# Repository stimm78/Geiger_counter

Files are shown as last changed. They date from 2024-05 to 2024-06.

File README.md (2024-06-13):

# Geiger Counter

 A Geiger counter is a practical electronic device used to measure ionizing radiation, and it is widely used in experimental physics and nuclear industries. Our goal for this project was to build a custom Geiger counter to measure the count rate of radioactive sources. After building the Geiger counter, we characterized various parameters of our device such as the dead time and tube efficiency. Using our device, we measured and compared the count rates of Co60 and Sr90 with attenuating materials placed in between the device and the radioactive source. 

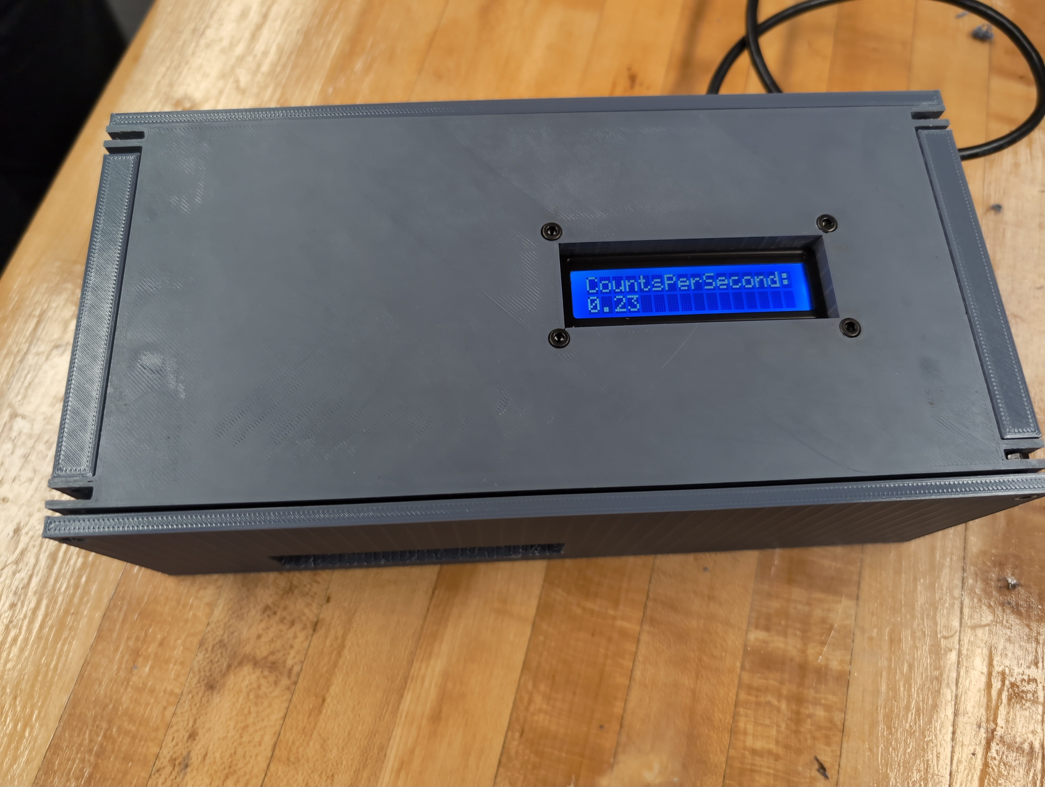
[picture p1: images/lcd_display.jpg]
alt test

  
  ## Table of Contents
* [Motivation](https://github.com/stimm78/Geiger_counter#motivation)
* [Theory](https://github.com/stimm78/Geiger_counter#theory)
* [Design](https://github.com/stimm78/Geiger_counter#design)
* [Device Characterization](https://github.com/stimm78/Geiger_counter#device-characterization)
* [Experiments](https://github.com/stimm78/Geiger_counter#experiments)
* [Acknowledgements](https://github.com/stimm78/Geiger_counter#acknowledgements)

## Motivation
The radiation we are observing is ionizing radiation, carriers of enough energy to ionize many common materials. The lower bound for this energy is considered to be about 10 eV, which encompasses alpha particles (He nuclei), beta particles (electrons), and gamma rays (photons). These subatomic particles are not visible to the naked eye; to verify their existence and our physical models of their behavior, it is necessary to build specialized nuclear detector devices such as our geiger counter.

 In particular, our group was interested in testing the drop-off of the intensity of nuclear radiation with distance and with material thickness. We expect that the radiation emitted from our sources are isotropic, so the intensity is expected to drop off as $1/r^2$, where r is the distance from the source. By modeling the attenuation of radiation as being attributed to random scattering/absorption by the atoms of an attenuating material, we should also expect the intensity of ionizing radiation should drop off exponentially as $I = I_0e^{\mu t}$, where $I_0$ is the initial intensity of the radiation,  is the linear attenuation coefficient of our material, and t is the thickness of our material.

## Theory 

### Geiger Muller Tube


A GM counter is a nuclear detector which is capable of detecting alpha particles, beta particles, and gamma radiation. To detect these ionizing particles, the geiger counter is specially designed to amplify the electrical discharge from one ionized atom and read this discharge as a voltage drop across a resistor.

The Geiger Muller counter is a metallic tube with a tungsten rod connecting the anode and cathode, filled with a gaseous mixture primarily composed of noble gas with some organic compound like ethanol mixed within it. When we connect the cylinder to the negative terminal of a high voltage source, a large voltage gap is generated between the tungsten and the metallic cylinder, creating a large electric field within the tube. When ionizing radiation enters the tube and ionizes an atom, the released electron is accelerated by the electric field, gaining sufficient kinetic energy to further ionize other atoms, whose electron offspring get accelerated by the electric field, which ionizes more atoms, etc.. This positive feedback loop of ionization is called the Townsend Avalanche, which amplifies the electrical discharge until the electrons reach the central electrode to move along the body of the circuit. Meanwhile, the positive cations leftover from ionization are pushed away from the central electrode towards the outer metallic cylinder. Our impulse of current will then run through a resistor, creating a measurable voltage drop measurable by a detector. The current will the move along back to the end of the tube, recombining with the positive charges lingering on the metallic cylinder and resetting our tube to take further measurements.

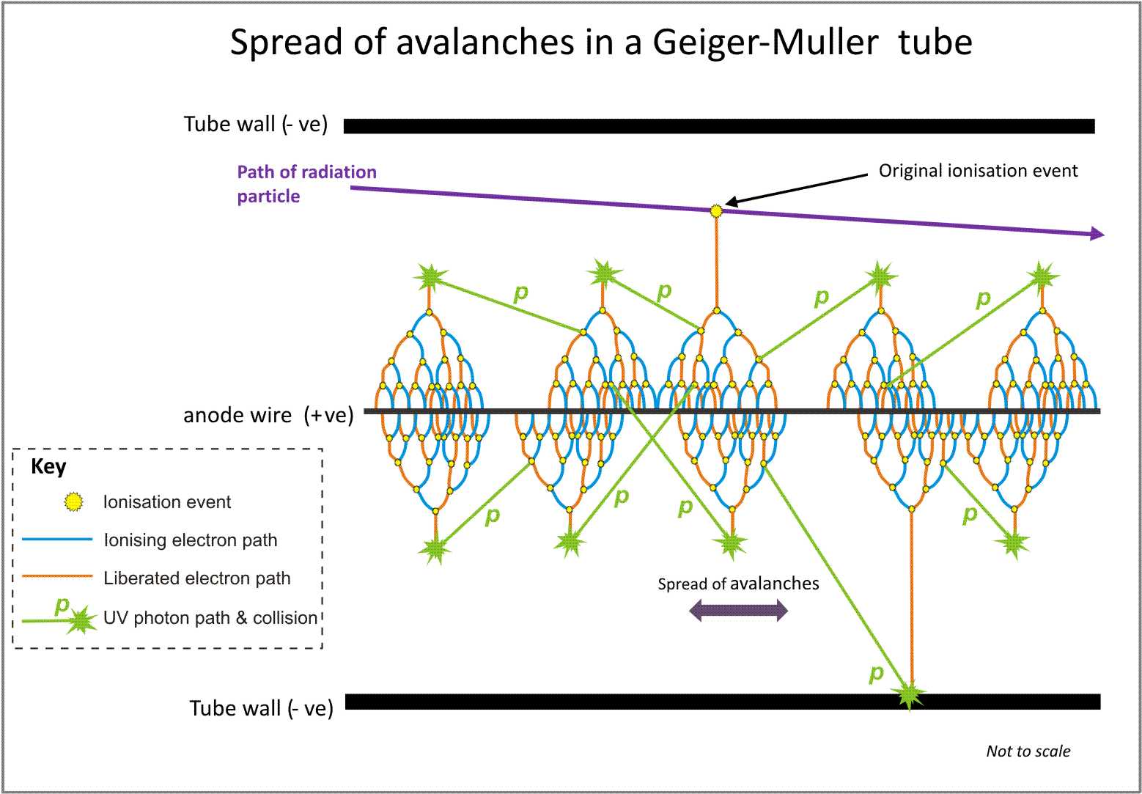
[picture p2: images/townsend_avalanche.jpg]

When ionizing radiation triggers the avalanche effect, the tube is temporarily unable to detect new radiation due to the time it takes for all the wonderful physics outlined above to run its course when a particle is detected. This temporary insensitivity to radiation is called the dead time of the counter. To maximize the reliability of our measurements, we should minimize the dead time. This is a key limitation to geiger counters - they are not accurate for extremely high counting rates, or equivalently when there are a high amount of nuclear particles striking the tube. Another limitation is that the Geiger counter cannot distinguish between the energies of two different nuclear particles; the current pulse generated by the tube is the same.

Some ionizing radiation will pass through the tube without ionizing any atoms, adding further uncertainty to our measurement of the radiation intensity. The ratio between the measured count rate from the geiger counter and the true one calculated from the activity level of our source is called the tube efficiency. This metric should be as high as possible to improve the reliability of our measurement.

Inverse Square Law Dropoff with Distance
If we model our radiation sources as emitting ionizing radiation isotropically, then necessarily the radiation emitted per second per steradians should be constant. Call this quantity I0. The area that some solid angle $\Omega$ consumes at a distance r is $\Omega r^2$; thus, the radiation emitted per second per unit area $I(r)$ is related to $I_0$ by

$$I(r)\Omega r^2 = I_0 \to I(r)=I_0/(r^2)$$

Thus, we should expect an inverse square law drop off in radiation intensity as we get further from a radioactive source.

Exponential Attenuation
Suppose that some $N(x)$ radioactive particles scatter off of the atoms within some infinitesimal thickness $dx$ with probability $\mu dx$, modeling the scattering cross section of the atoms within this slice of material. Then the number of radioactive particles remaining after scattering off of our slice of material is

$dN = -Ndx$, so then calling $N(0) = N_0$ and solving for $N(x)$
$$dN/N= -\mu dx \to ln(N/N_0)=-\mu x \to N(x)=N_0e^{-\mu x}$$
Thus, if our attenuating material is t long, then the number of radioactive particles that remain after passing through our material is
$N = N_0e^{-t}$, which naturally implies that $I = I_0e^{-t}$

## Design
### [Parts List](https://docs.google.com/spreadsheets/d/1FQi-imXlj1l_IscpUjg6qlx7No3eN8g5/edit?usp=sharing&ouid=113398199388474590846&rtpof=true&sd=true)

### Circuit Diagram
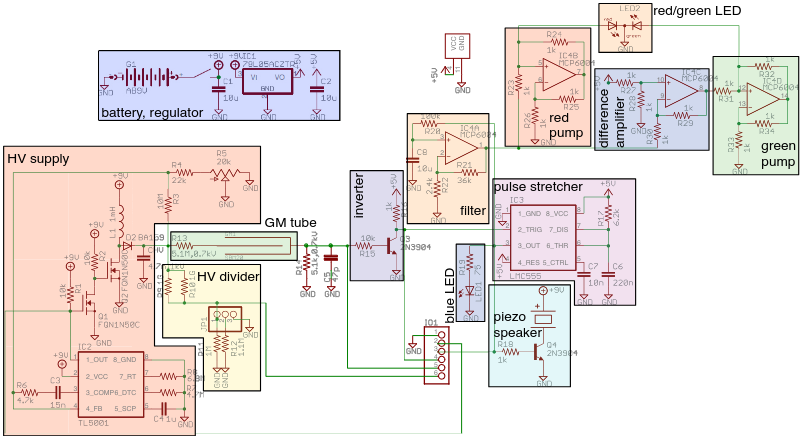
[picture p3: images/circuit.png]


We used a 9V battery source to power the circuit. The HV supply is achieved using a boost converter (TL5001) which steps the voltage up to 400V as required by the GM tube. When ionizing radiation is detected, the GM tube emits a current pulse which can be converted into a voltage pulse through a 5.1 kOhm resistor. The inverter is a BJT that acts as a switch to invert the voltage pulse.  Since these pulses are extremely short, the pulse stretcher (555 timer) converts the original pulse into a 1.5ms long square pulse. The blue LED will flash and the piezo speaker will click whenever a pulse is detected. The filter
smooths out voltage pulses and produces a voltage that is proportional to the count rate. The red and green current pumps convert the filtered voltage to a proportional current. The difference amplifier subtracts the filter voltage from a reference voltage, which causes the green LED to fade as the count rate increases. The RG LED serves as a visual indication of the count rate, with red corresponding to a high count rate and green corresponding to a low count rate.
### PCB
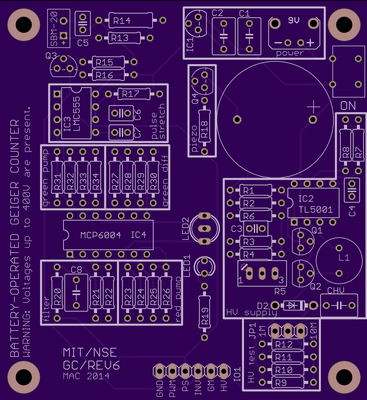
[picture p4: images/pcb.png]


We assembled these components onto a PCB that was designed and made available by [MIT](https://ocw.mit.edu/courses/22-s902-do-it-yourself-diy-geiger-counters-january-iap-2015/pages/labs/), with modifications to the HV supply in order to achieve the desired boost voltage. It turns out that the components around the HV booster designed by MIT do not work with the TL5001 chip, and we had to modify several components around the HV supply. We changed the resistors in the diagram to the following values: R8 = 500 KOhm, R7 = 460 KOhm, R4 = 10KOhm; Potentiometer: 10KOhm; R3 = 6.4 MOhm. This gave a range of voltage values across the GM tube from 320V to 480V, which we could tune using the potentiometer. The GM tube we used is the SBM-20 GM tube, which has an operating voltage range of 375-475 Volts.



### Counting Rate
The expected count rate is the inverse of the average time between counts (these times follow an exponential distribution; see Experimental Method). We used an Arduino UNO to calculate the difference in times between counts and determine the displayed rate. The rate considers the 20 latest counts, allowing it to update to any changes in its surroundings. To compensate for any sharp decrease in count, the rate removes the oldest count from consideration after twice the average of the considered times (for the exponential distribution, this time is equal to the average time plus one standard deviation). To display the counting rate, we used an LCD connected to the Arduino.

### 3D Printed Case
We 3D printed a case to contain and mount the parts of our counter. It is composed of three parts: the base, with inserts for the PCB, Arduino, battery holder, and GM tube clips; the outer case, with the outer face of the GM tube window approximately one inch away from the GM tube; and the lid, with an insert for the display.

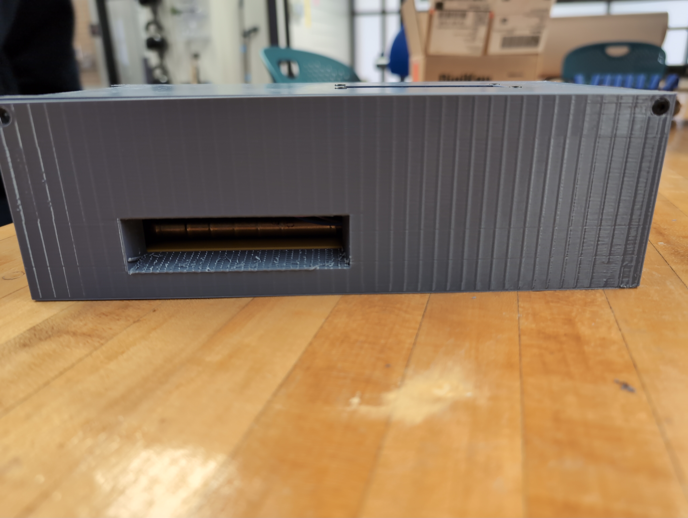
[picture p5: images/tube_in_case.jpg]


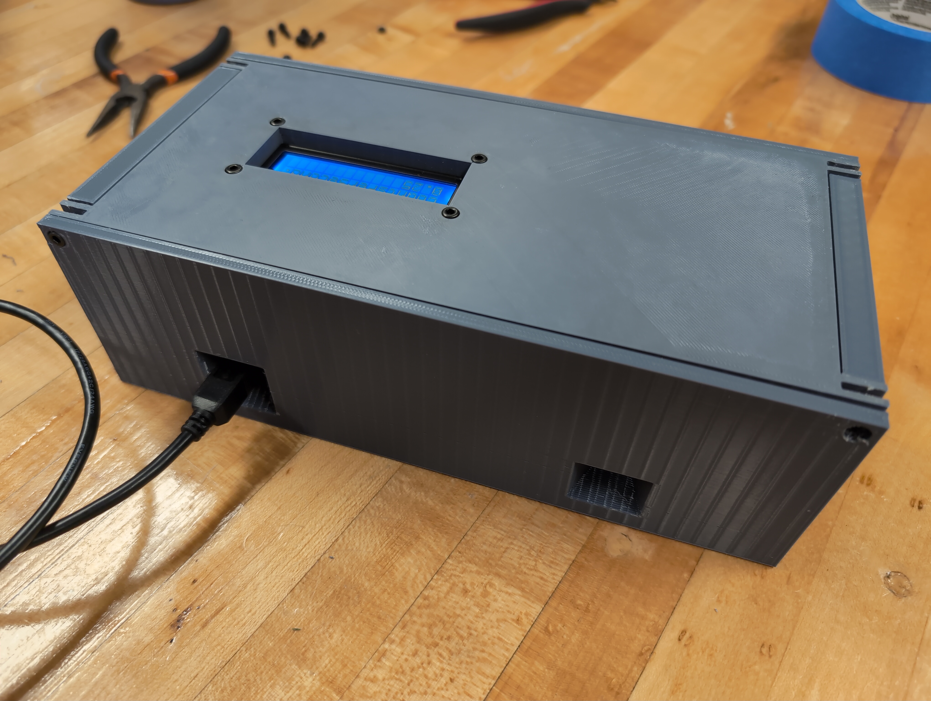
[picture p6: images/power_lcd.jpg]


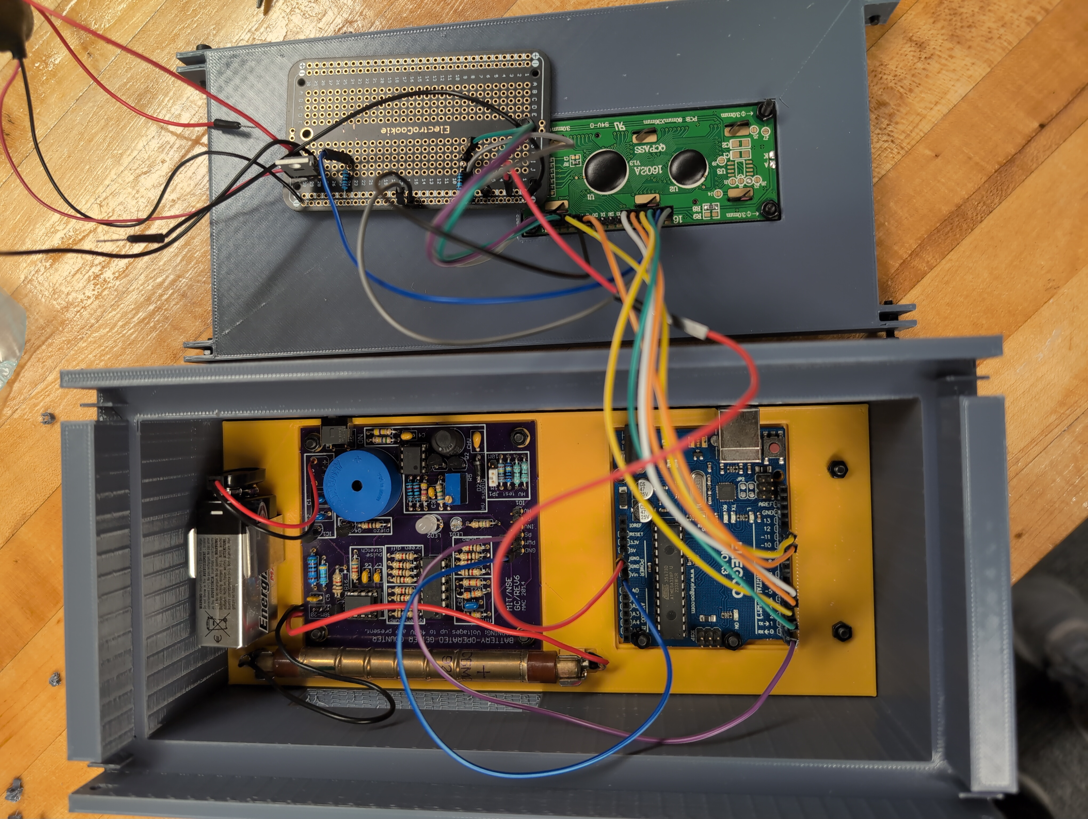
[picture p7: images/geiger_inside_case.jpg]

## Device Characterization
To verify the effectiveness of our measurements, we characterized our geiger counter by measuring its tube efficiency and dead time.
### Dead Time
In order to measure the dead time of the GM tube, we placed a source of Sr90 as close to the tube as possible (approximately 1 mm). We then connected the PCB to the oscilloscope and measured the smallest time between pulses. The dead time of the GM tube at 400V was measured to be approximately 500 microseconds, which is reasonable given the minimum dead time of 190 microseconds according to the [SBM20 data sheet](https://www.gstube.com/data/2398/).
The effective dead time of the counter is larger due to the pulse stretcher; the oscilloscope gave a time of about 1.76 milliseconds.

### Tube Efficiency
The PCB has a potentiometer to tune the voltage across the GM tube. Although the data sheet says that the tube has an operating voltage range of 350-475 volts, we wanted to determine the optimal voltage to maximize tube efficiency. To find the tube efficiency, we calculated the expected count rate of Sr90 using its labeled true activity and its solid angle relative to the tube. For Sr90, the expected count rate turned out to be approximately 20.4 counts/second when placed 10 cm away from the tube.

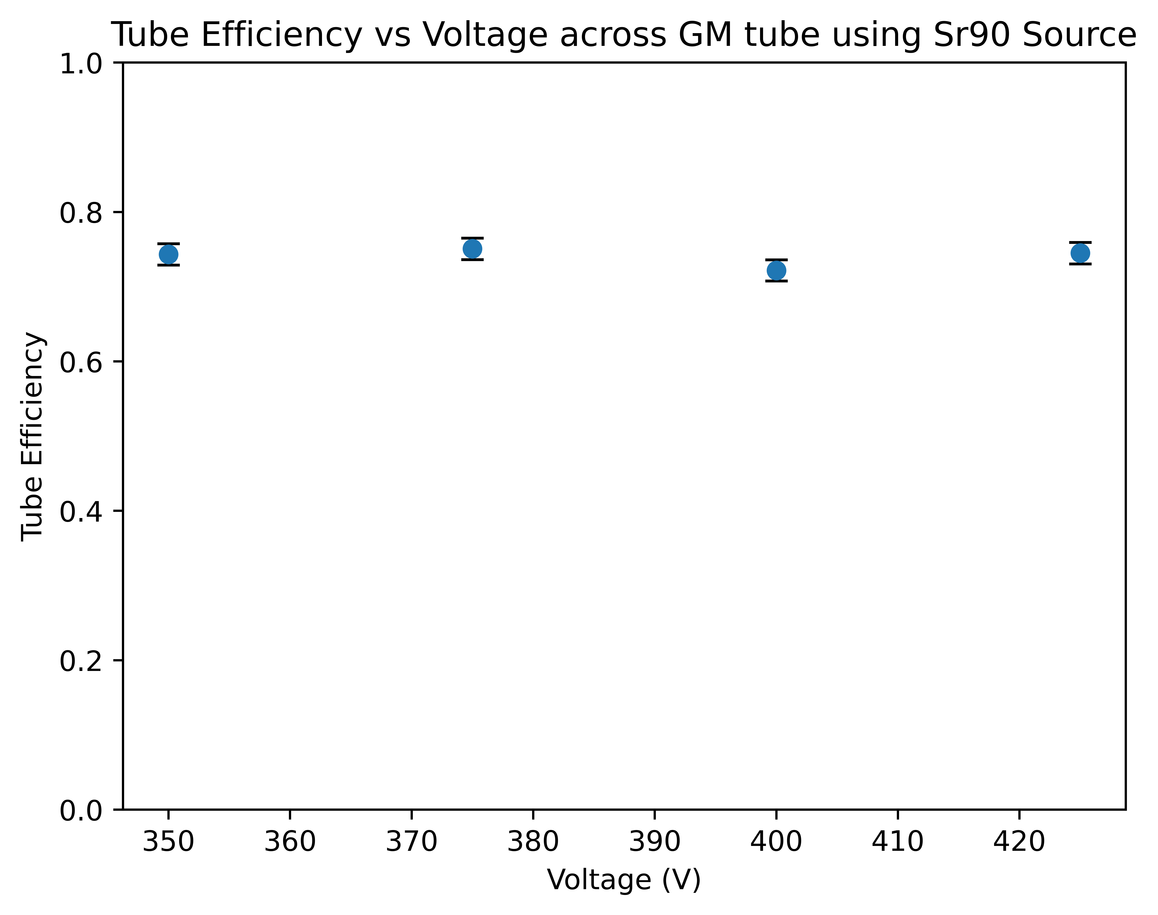
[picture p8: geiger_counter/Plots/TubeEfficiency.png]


As shown in the plot, the tube efficiency did not vary too much based on the voltage. The range of efficiencies went from 0.738 to 0.770, with the “optimal” voltage near 375V.
## Experiments
### Radioactive Sources
<sup>59</sup>Co + n &rarr; <sup>60</sup><sub>27</sub>Co &rarr; <sup>60</sup><sub>28</sub>Ni + e<sup>-</sup> + 2 $\gamma$

<sup>90</sup><sub>38</sub>Sr &rarr; <sup>90</sup><sub>39</sub>Sr + e<sup>-</sup> + $\nu$<sub>e</sub>

We tested our Geiger counter using two radioactive sources: Co60 and Sr90. As shown in the equations, Co60 emits beta and gamma radiation while Sr90 emits only beta radiation.

### Experimental Method
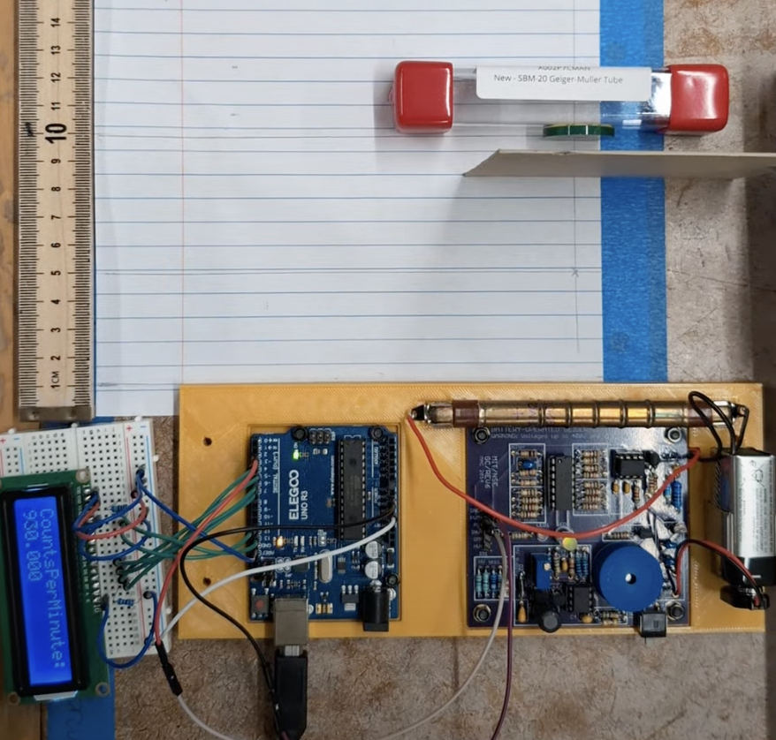
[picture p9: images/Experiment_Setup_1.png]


Unlike the display rate, the rate calculated from a measurement acquisition assumes none of the factors affecting count rate change over the measurement period, allowing estimation of the count rate for that specific environment. The measured values are the differences in time between when counts are read, which are obtained through the Arduino’s serial communication. Since we expect that radioactive decays occur randomly and independently (at least for a small measurement period relative to the half-life), the time between counts $t$ should follow an exponential distribution, with probability density $f(t)=re^{-rt}$, where $r$ is the count rate we wish to obtain. We used a maximum likelihood estimation (MLE) with this distribution to calculate $r$, which finds the value of $r$ for which the probability of getting the measured data set is maximized. Provided the data does indeed follow this exponential distribution, the calculated rate will be close to the average rate predicted by the data set.
By varying factors like distance and shielding between these measurements, we can characterize the effect these factors have on the count rate. It is critical to subtract the background rate from the resulting rates in order to isolate the effect of the independently varied factors.

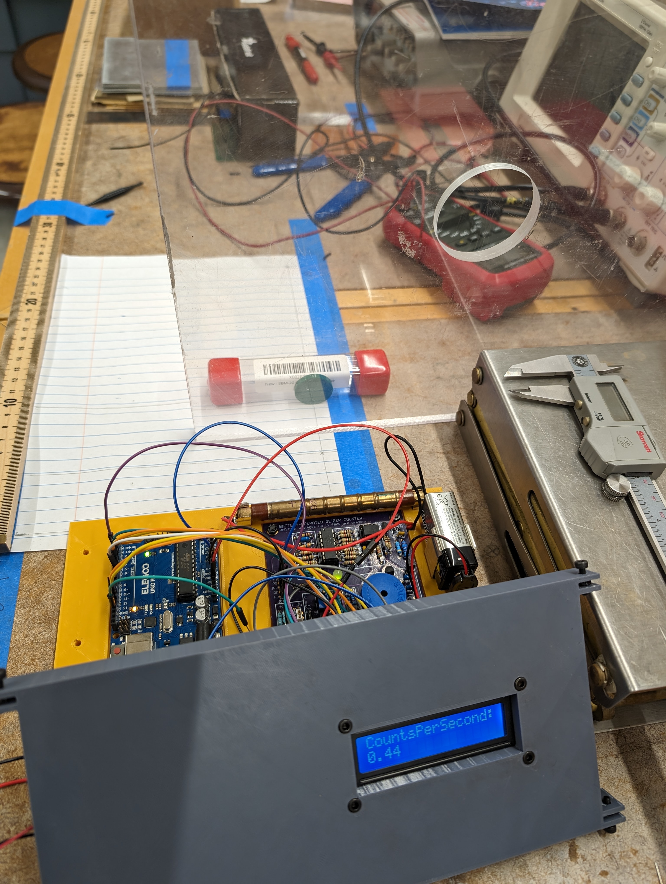
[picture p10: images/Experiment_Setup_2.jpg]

### Distance Tests
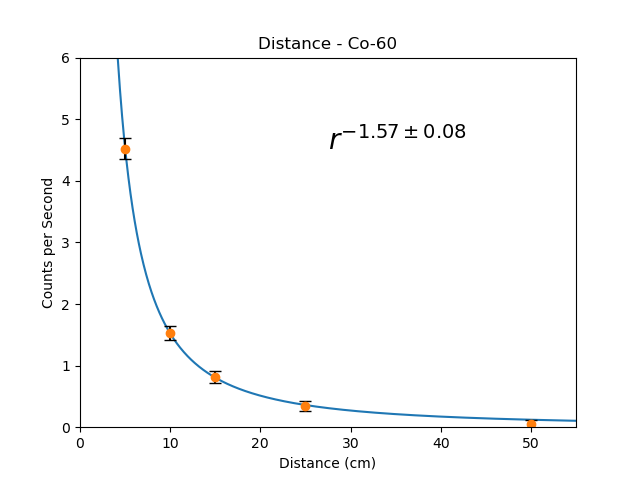
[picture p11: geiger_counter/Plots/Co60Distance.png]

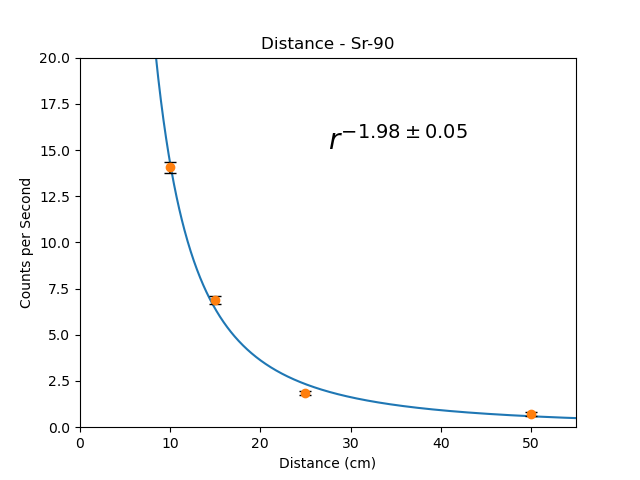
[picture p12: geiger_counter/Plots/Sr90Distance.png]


To test the inverse square law drop off of intensity with distance, we measured the counts per second from a Cobalt-60 source and Strontium-90, varying the distance from 5 cm to 50 cm. At a distance of 5 cm, the counts from the Strontium source were rapid enough to exceed the counter’s dead time, resulting in inaccurate measurements. The plots below fit to power laws close to $1/r^2$, providing strong validation for our theory.

### Shielding Tests
#### Beta Shielding
| Material | Sr90 Count Rate (cps)| Co60 Count Rate (cps)|
| :---------------- | :------: | ----: |
| None | 14.06 | 1.53 |
| Lead (1.21 mm) | $\approx$ 0 | 1.72 |
| Lead (3.23 mm) |  $\approx$ 0  | 1.39 |
| Plexiglass (12.7 mm) | $\approx$ 0 | 1.38 |

Radiation shielding does not necessarily indiscriminately block all radiation, as illustrated by some of the materials above. Though Strontium-90 gives a much higher count rate in the absence of shielding, the Geiger counter’s measurement drops to close to the background rate when the source is shielded by lead or plexiglass. This is not the case for the Cobalt-60 source, implying that its radiation has some property the Strontium-90’s does not. This is indeed the case: Cobalt-60 also produces gamma rays, which are much harder to attenuate given their higher energy and lack of charge.

## Acknowledgements
This project was made for Phys CS 15C lab at UCSB. Contributors are Deven Tseng, Aditya Chezhiyan, and Brian Chang.

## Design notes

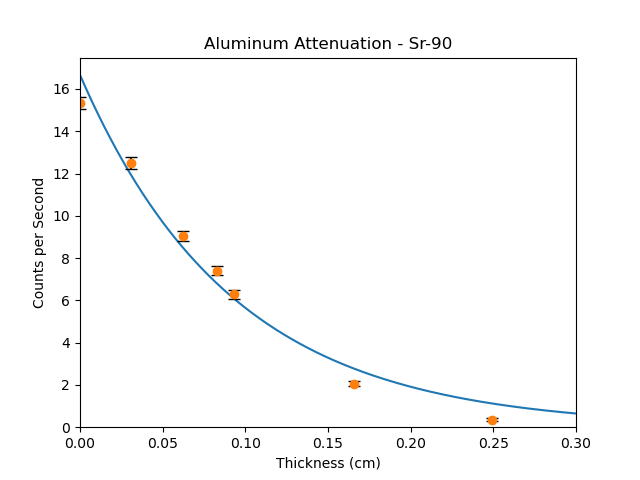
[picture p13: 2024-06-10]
geiger_counter/Plots/AlAttenuationSr.png

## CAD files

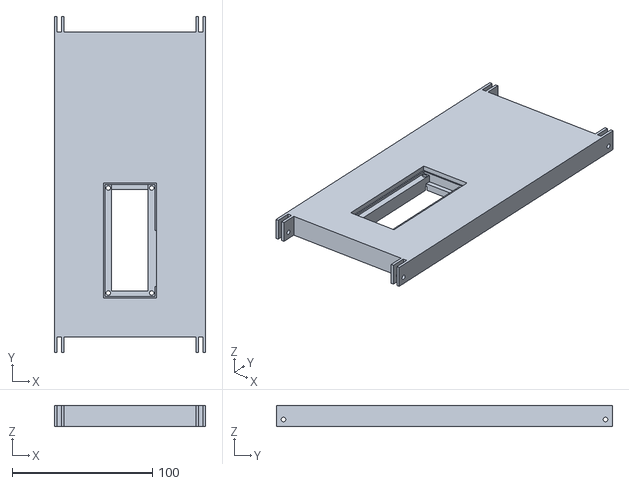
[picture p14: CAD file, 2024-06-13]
geiger_counter/Case/Lid v3.stl
108.0 x 240.0 x 15.0

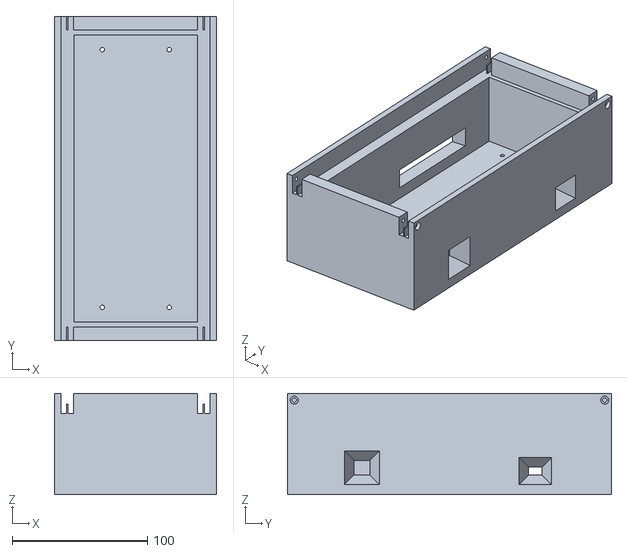
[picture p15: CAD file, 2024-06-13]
geiger_counter/Case/GeigerCounterCase v3.stl
120.0 x 240.0 x 75.0

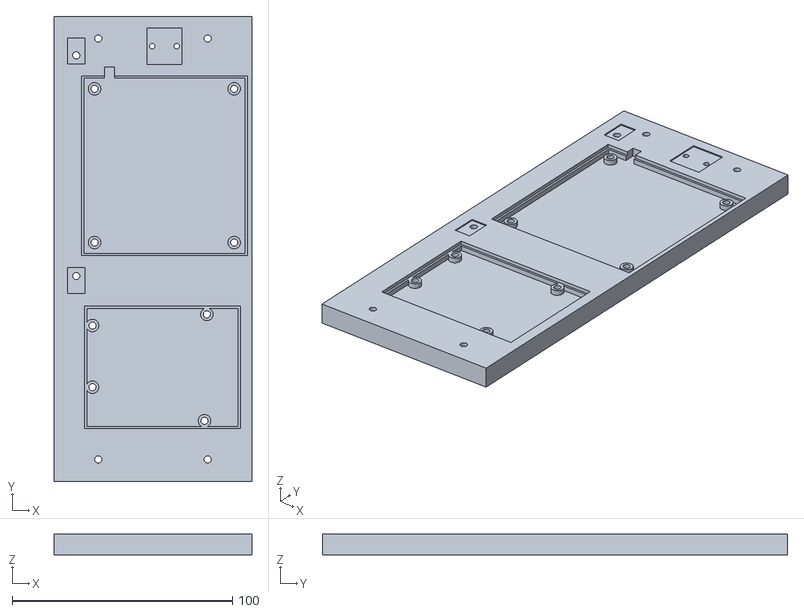
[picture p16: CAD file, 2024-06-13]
geiger_counter/Case/Geiger Counter Base v2.stl
89.6 x 210.9 x 9.43

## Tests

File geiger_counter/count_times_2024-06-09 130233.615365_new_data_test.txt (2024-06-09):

Rate (cps): 0.385857557617794
Error: 0.04611879919926816
0.119828
0.031684
0.016512
1.902956
0.774532
1.489916
3.10648
1.143204
0.348092
4.851612
1.48576
3.476096
0.898372
5.815396
0.614488
1.459216
1.9894
2.937644
13.568908
0.434324
0.580204
1.987304
4.710844
3.661452
2.600052
6.851568
0.992756
6.311472
2.959212
1.724312
3.043748
1.300044
3.73502
2.033276
1.429008
4.893448
2.916268
2.074488
1.848108
4.51466
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

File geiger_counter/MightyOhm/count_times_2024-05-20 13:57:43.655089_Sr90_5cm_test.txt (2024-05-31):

0.615696
1.51852
2.329724
6.983268
7.230768
7.621256
8.286676
8.66162
8.805232
9.231008
10.756436
10.75654
10.75772
10.75782
10.759276
10.759376
10.75948
10.759588
10.759632
10.7597
10.759872
10.759972
10.76044
10.76054
10.760756
10.760856
10.761008
10.761188
10.761704
10.761768
10.761832
10.761896
10.76196
10.978316
10.978412
11.212828
11.212928
11.213164
11.213264
11.213656
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

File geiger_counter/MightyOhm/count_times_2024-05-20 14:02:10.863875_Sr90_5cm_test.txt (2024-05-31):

1.087376
1.087476
4.632284
4.632384
4.694604
4.694704
7.628908
7.629008
8.218432
8.218532
9.01498
9.01508
9.600776
9.600876
9.602088
9.602188
9.60242
9.60252
9.602564
9.602628
10.11896
10.119416
11.002688
11.002788
11.009584
11.009684
11.01294
11.01304
11.014836
11.014936
11.55708
11.55718
11.557224
11.557304
12.091508
12.091608
12.28848
13.644508
13.644608
13.90638
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

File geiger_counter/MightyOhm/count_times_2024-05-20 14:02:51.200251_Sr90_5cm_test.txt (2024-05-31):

38.673184
38.673284
39.094664
39.094764
39.659356
39.659456
39.706576
39.706676
39.90962
40.810148
40.810248
40.81752
40.81762
42.116076
42.116176
42.361192
42.361288
42.737424
42.737524
42.817304
42.817404
43.465672
43.465772
44.014512
44.014612
44.314684
44.314784
44.809204
44.809304
45.158688
45.158788
45.27688
45.27698
46.165304
46.165404
47.148484
47.148584
47.148628
47.14872
47.149964
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

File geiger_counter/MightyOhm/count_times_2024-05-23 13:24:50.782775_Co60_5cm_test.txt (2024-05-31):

0.174296
0.433552
0.698596
183.366656
188.870656
206.954496
428.808192
428.971008
429.051904
429.17888
429.239296
429.290496
429.539328
429.5936
429.623296
429.684736
429.712384
429.83424
429.861888
429.888512
429.91616
429.94688
429.979648
430.006272
430.419968
430.436352
430.190592
430.206976
502.49216
558.338048
600.274944
614.788096
734.783488
859.441152
862.441472
876.304384
884.72064
885.151744
885.24288
885.308416
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

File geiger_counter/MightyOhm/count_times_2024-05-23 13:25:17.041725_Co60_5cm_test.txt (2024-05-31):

0.792184
0.919312
0.939092
1.318544
1.885808
2.047788
2.048724
2.261796
2.267516
2.2684
2.361584
2.361784
0.00276
3842.244644
2839.019556
1552.154661
2012.217395
2070.675511
2082.734135
2678.849591
2047.082554
1230.766139
3012.558909
3751.018565
2458.124359
2690.646089
2767.454281
2796.027977
2857.631817
2964.586569
3034.316873
3101.425737
3125.805129
3147.563081
3182.690377
3213.361225
3224.371273
3231.449161
3247.439945
3257.139273
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

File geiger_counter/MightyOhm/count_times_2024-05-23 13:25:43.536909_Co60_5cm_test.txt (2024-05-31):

0.082156
0.365064
0.420068
0.637088
0.669904
0.859344
0.978432
0.979236
0.981096
1.209956
1.24158
1.28832
1.597596
2.839252
2.974564
3.114968
3.223608
3.801876
4.155188
4.234564
4.2355
4.235688
4.768504
4.966708
5.282908
5.316532
5.626912
5.627028
5.627232
5.62738
5.627764
5.627976
5.628168
5.628316
5.628424
5.628532
5.628688
5.628832
5.629004
5.629112
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
